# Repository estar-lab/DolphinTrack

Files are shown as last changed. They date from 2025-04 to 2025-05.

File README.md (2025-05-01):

# DolphinTrack

## Computer Vision: Dolphin Detections
`camera_detection`: Includes computer vision pipeline for visual tracking of dolphins. 
- `evaluation`: compares ground truth and tracked coordinates for model performance
- `inference`: pre-trained models, preliminary results, scripts for running different model architectures on input video
- `scripts`: utility files for batching to mitigate RAM issues, prompting for SAM-based models, particle filter to fill in trajectories
- `training_pipeline`: labeled datasets, scripts for fine-tuning model architectures on custom data 

## RF Positioning System: Custom Tag and Anchor Communication 
`RF_localization`: Includes code for ultra-wideband positioning system.
- `anchor_tag_stm32`: code for tag and anchor boards
- `lora_server`: example code for computing position using range transmitted over LoRa
- Also includes BOM, circuit schematics, and CAD for tags and anchors

## Association Demo: Live Person Detection and Localization 
`person_demo`: Includes complete pipeline for real-time detection and tracking of people, with stable association for tagged person.

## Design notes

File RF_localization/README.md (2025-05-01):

# RF Localization Code

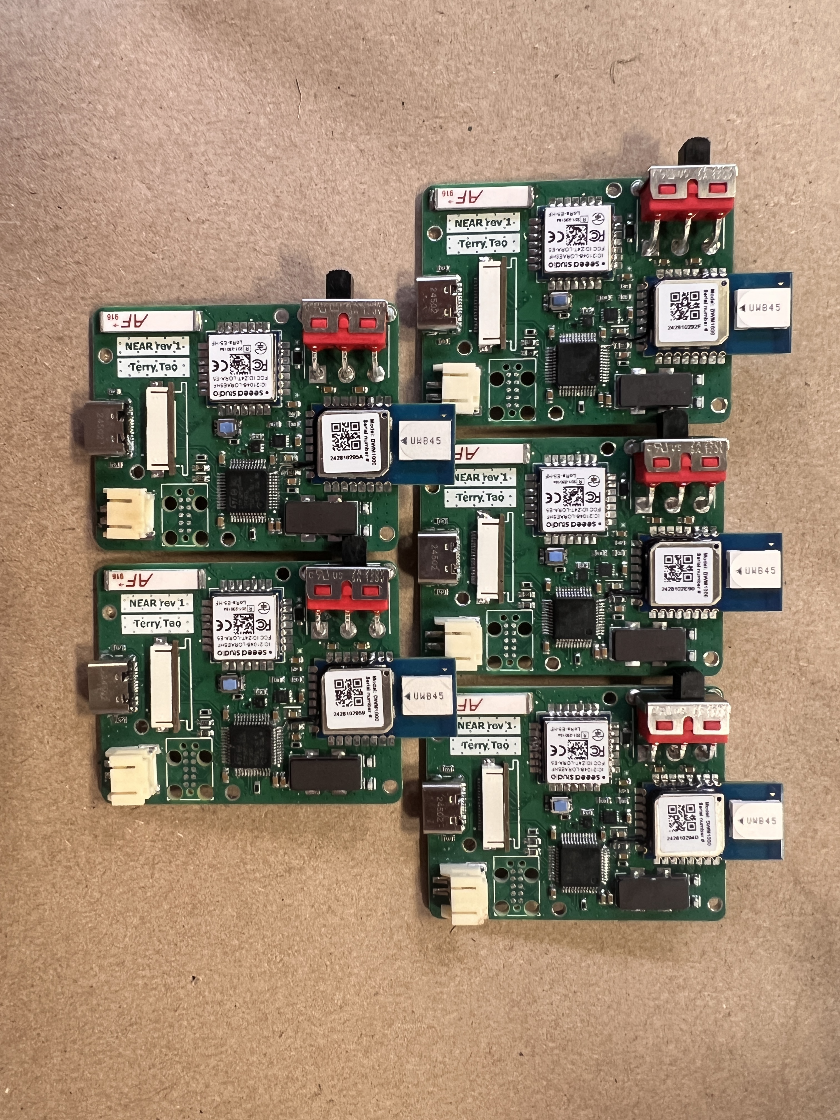
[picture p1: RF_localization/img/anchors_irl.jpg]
anchor_pcbs

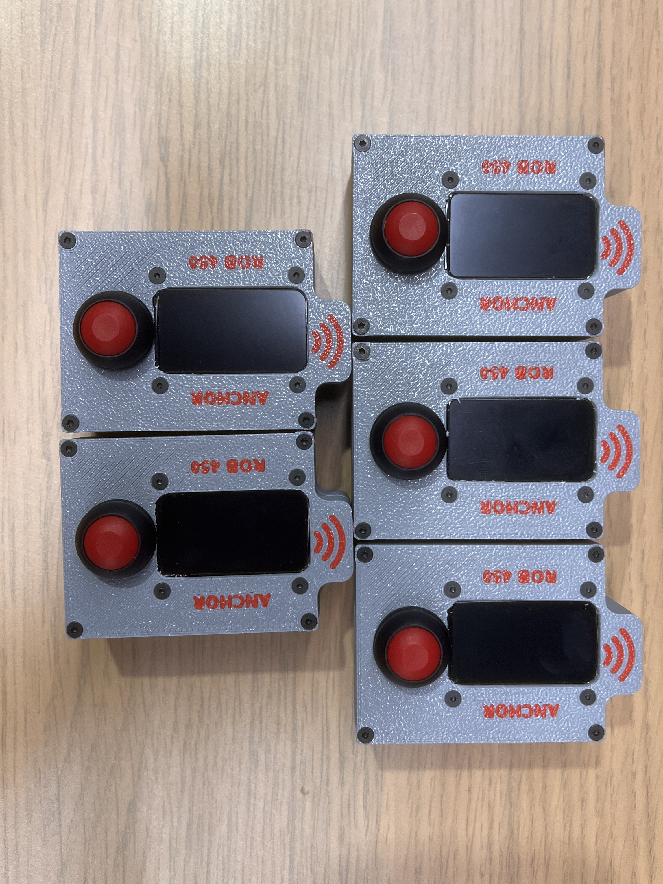
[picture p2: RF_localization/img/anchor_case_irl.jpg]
anchors

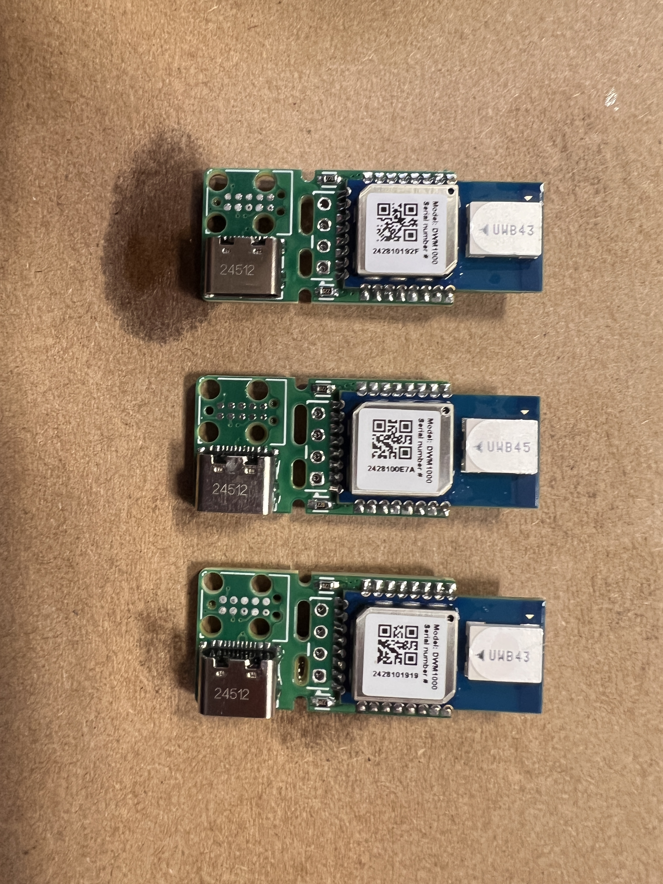
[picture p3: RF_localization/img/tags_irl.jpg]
tags


### anchor_tag_stm32 is for flashing the anchor and tag boards, lora_server is for using the Wio-E5 to receive LoRa messages on the positioning computer. These folders contain more information about setting up software.

### Revisions were made to anchor pcb:

- Reset pin on the DW is now connected to the STM on pin 12
- Screen power mosfet deleted, screen is now powered through two GPIO pins on the STM
- JTAG pogo pin pads moved to the bottom side to make flashing easier when pcb is packaged in case
- 13k pulldown on the ILIM/VSET pin of the BQ instead of 18k to allow for 1.1A battery charge current instead of 0.5A
- 10k pulldown on the TS/MR pin of the BQ bypasses the thermal check to always charge when there is a 5V supply
- Charge diode deleted, originally intended to allow charging when switch is off, didn't work because BQ does voltage regulated charging

### Notes for anchor case assembly:

- The gerber files work for pcbway, layer stack is [SIG TOP, GND, PWR, SIG BOT], and are updated to rev. 2 of the anchor
- Screens are extremely delicate, use caution when pushing on the back because they will crack.
- Bend the button solder terminals 90deg then solder the button wire under them, otherwise the terminal will hit the anchor pcb
- The batteries ship with 2.54 JST, need to recrimp with PH 2.0

### Recommended future changes

- Use a fourth DW message from the anchor to the tag to transmit the calculated range to the tag. UWB transmit rate is much faster than LORA so you can log the position data on the MTAG SD card at a higher rate than the LORA server could receive.
- Change the STMF0 to a faster microcontroller, the DW SPI clock speed is currently 18MHz and this can be increased to at least 20MHz. We have seen forum posts where people have used up to 30MHz, so this is worth trying. (Look out for AndyA on the Decawave forums, he is the goat)
- Glass cover on the anchor case to prevent accidental screen damage
- Automatic anchor position calibration tool. We think the process for anchor calibration should be graphical, where the user proposes estimated anchor positions, then the tool optimizes the graph based on actual anchor-anchor ranges. Additionally, a calibration initialization message would have to be sent to the anchors, probably over LORA downlink to kick them into calibration mode. In calibration mode, the anchors should poll with a timeout then initialize TWR to the next higher anchor ID.
- For changing the STM to an ESP, we recommend modifying port.h to use the ESP HAL library, and deleting any STM autogenerated HAL includes. The other option is to use thotro/arduino-dw1000 library, which we have not tested.

### Recommended anchor placement at Dolphin Quest Oahu:

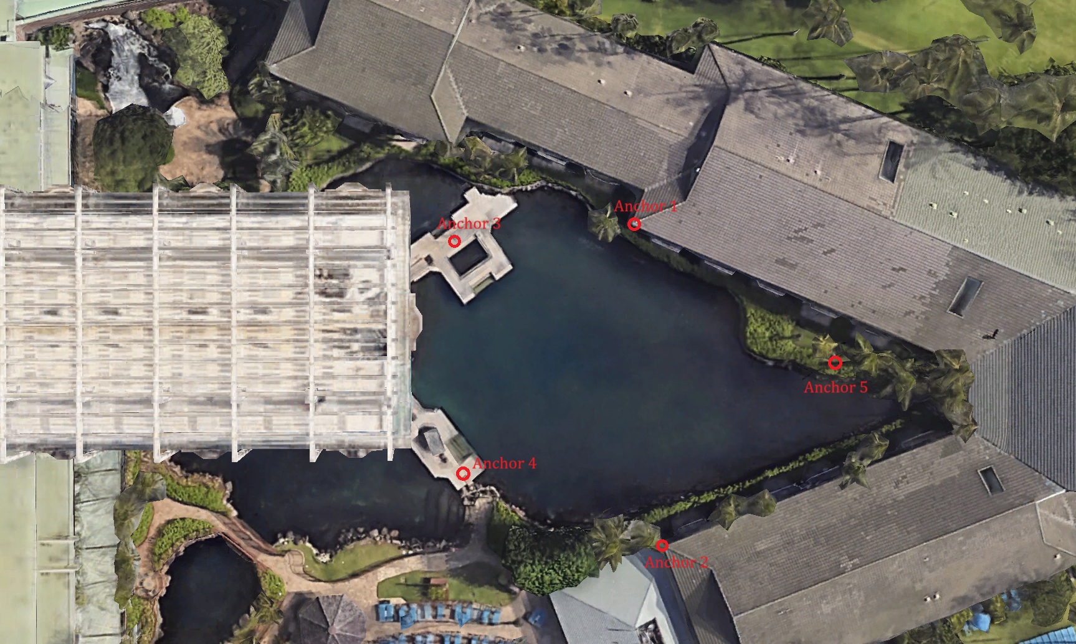
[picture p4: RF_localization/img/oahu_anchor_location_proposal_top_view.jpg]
anchor location proposal top

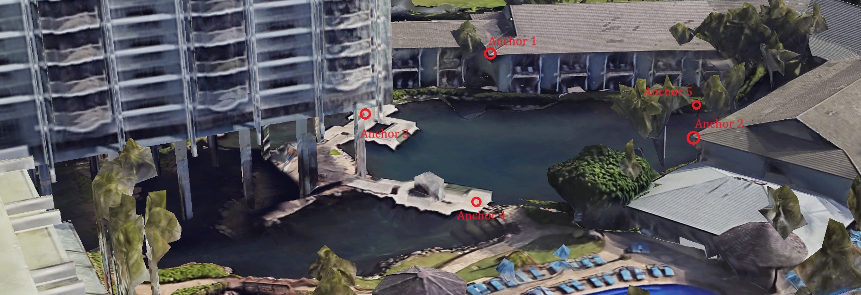
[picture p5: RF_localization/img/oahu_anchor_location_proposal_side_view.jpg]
anchor location proposal side


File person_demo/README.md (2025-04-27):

# Rob 450 Person Tracking Demo 
This code will run a live demo of person tracking intended to demonstrate the efficacy of the DolphinTrack association system 
in a testing environment. 

## Hardware Requirements 
- ZED camera: Used to record video of the testing environment 
- NVIDIA Jetson: Used to run ZED SDK for real-time tracking
- RF tags and anchors: Used for retrieving position coordinates
- Laptop: Used to display particle filter for coordinates received by Jetson 

## Usage 
`association_demo.py`: Used for camera tracking, RF positioning, and association 
- Outputs live video stream of tracked people in camera FOV, each with a unique ID
- Prints live world frame coordinate of person holding RF tag
- Re-associates tagged person, combining camera and RF position to display red bounding box with ID 0
  
`particle_filter.py`: Used for plotting real-time position of tagged person in world frame 
- Receives world frame coordinates of tagged person
- Plots real-time motion of tagged person in world frame 

## Applications 
- Handles dropout and identity switches for tracking scenarios, maintaining consisted ID for tagged person
- Will be used in the field for dolphin tracing and association

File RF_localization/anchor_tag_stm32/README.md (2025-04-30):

# STM32 Anchor and Tag Code

### Setup
1. Clone this repository.
2. Download the STM32CubeIDE (available at https://www.st.com/en/development-tools/stm32cubeide.html).
3. Navigate to `File` -> `Open Projects from File System` -> `Directory`, select this directory (anchor_tag_stm32) in the file system, and click `Finish`.
4. The project should now show up in the `Project Explorer` on the left side of the screen as `NEAR_ANCHOR`. Press `Ctrl+B` or `Project` -> `Build All` to build.

The code for ranging is located in the `Core/` folder. Use the definitions in `Core/Inc/main.h` to determine whether the tag or anchor code is built. The tag and anchor ID's can be configured in `Core/Inc/id.h`. When the STLINK (included with the hardware) is attached to the tag or anchor, press the green play button to flash the device.

### Resources
* This codebase is adapted from the example code available at https://www.decawave.com/wp-content/uploads/2019/01/dw1000_api_rev2p14.zip.
* The DW1000 user manual provides detailed information on using the chip and ranging applications (https://www.qorvo.com/products/p/DW1000#documents).
* The Qorvo forum (https://forum.qorvo.com/tags/c/wireless-connectivity/ultra-wideband/5/dw1000) and in particular the user AndyA (https://forum.qorvo.com/u/andya/summary) made this project possible.
* Information on the LoRa module can be found on the Seeed Studio Wiki (https://wiki.seeedstudio.com/wio_e5_class/).

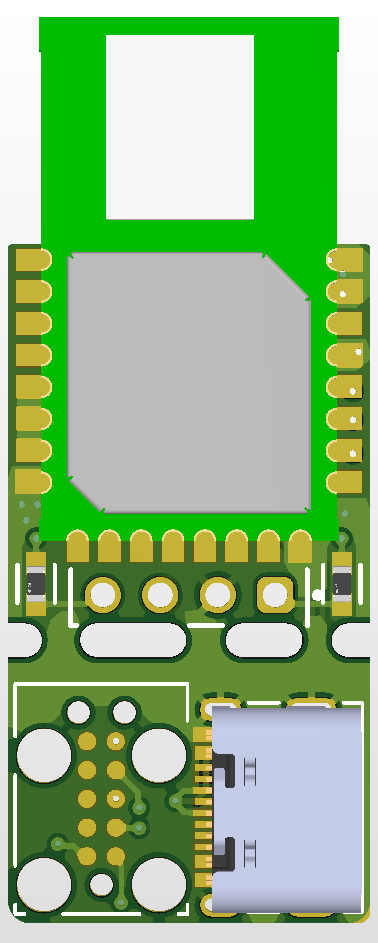
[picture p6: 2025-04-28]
RF_localization/ecad/tag/NEAR_DAUGHTER.png

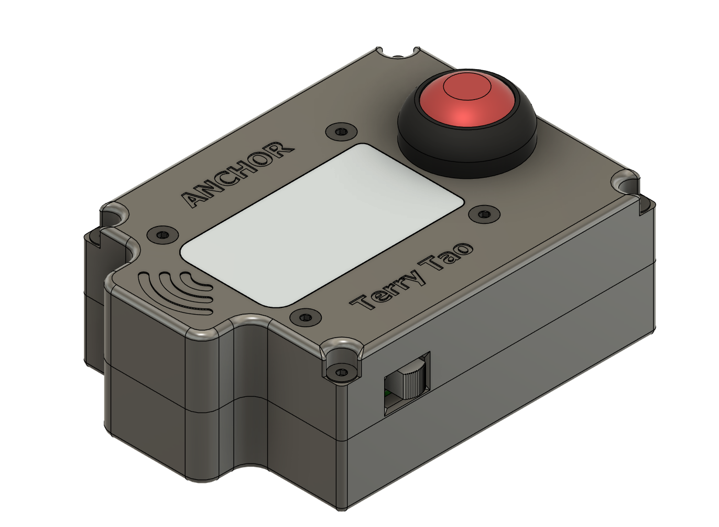
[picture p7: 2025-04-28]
RF_localization/ecad/anchor/CAD_1.png

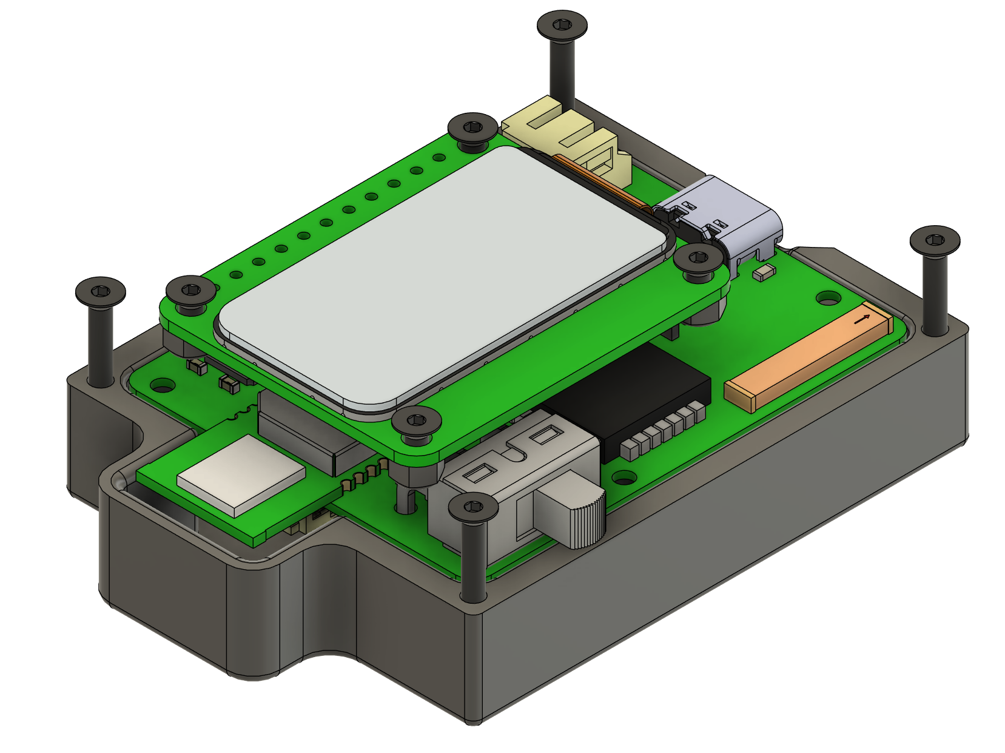
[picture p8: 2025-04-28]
RF_localization/ecad/anchor/CAD_2.png

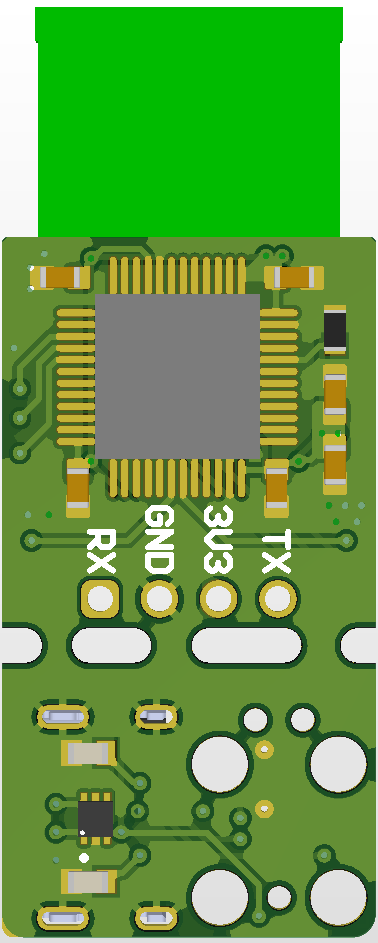
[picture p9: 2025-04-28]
RF_localization/ecad/tag/NEAR_DAUGHTER_BOT.png

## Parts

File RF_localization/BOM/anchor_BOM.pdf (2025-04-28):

Line # | Name | Description | Designator | Revision ID | Revision State | Revision Status | Quantity | Manufacturer 1 | Manufacturer Part Number 1 | Manufacturer Lifecycle 1 | Supplier 1 | Supplier Part Number 1 | Supplier Unit Price 1 | Supplier Subtotal 1
| 1uF | Cap Ceramic 1uF 25V X7R 10% Pad SMD 0603 125C Automotive T/R | C1, C2, C6, C7, C8, C9, C10, C11, C13, C14 | CMP-001-00097-1 | Draft | Up to date | 10 Murata | | GCM188R71E105KA64J | Volume Production | Newark | 66AJ7155 | 0.088 | 0.88
| C0603C120J5GACTU | Ceramic Capacitor 12Pf 50V, C0G, 5%, 0603, Full Reel | C4, C5 | CMP-2006-03703-3 | New From Design | Up to date | | 2 KEMET | C0603C120J5GACTU | Volume Production | Newark | 19C1214 | 0.007 | 0.014
| GRM188R60J106ME47D | Chip Multilayer Ceramic Capacitors for General Purpose, 0603, 10uF, X5R, 15%, 20%, 6.3V | C12 | CMP-2006-02792-2 | New From Design | Up to date | | 1 Murata | GRM188R60J106ME47D | Volume Production | Newark | 24R6334 | 0.065 | 0.065
| TC2050-IDC | CBL PLUG-OF-NAILS 10-PIN W/ LEGS | DBG1 | CMP-002-00071-4 | Draft | Up to date | | 1 Tag-Connect | TC2050-IDC | Volume Production | Digikey | TC2050-IDC-ND | 39 | 39
| ANT-916-CHP-T | 915 MHz Monopole Ceramic Chip Antenna | E1 | CMP-00025-00008-1 | Draft | Up to date | | 1
| 52746-1871 | 0.5 mm Pitch Easy-On(TM) Type FPC Connector, 2.0 mm Mated Height, Right Angle, ZIF, SMT, Bottom Contact, 18 Circuits, -20 to 85 degC, ELV and RoHS Compliant, Tape and Reel | J1 | CMP-1241-00380-1 | Released | Up to date | | 1 Molex | 52746-1871 | Volume Production | Newark | 37AC1285 | 1.29 | 1.29
| 2171790001 | USB Type C -Connector, Top-mount SMT, 16pos | Molex Incorporated 217179-0001 | J2 | CMP-002-00656-1 | Draft | Up to date | | 1
| S2B-PH-SM4-TB | Connector Header Surface Mount, Right Angle 2 position 0.079 (2.00mm) | P1, P2 | CMP-002-00662-3 | Draft | Up to date | | 2
| CPF0603B22RE1 | RES SMD 22Ω 0.1% 1/16W 0603 | R1, R2, R3 | CMP-03211-007811-1 | New From Design | Up to date | | 3 TE Connectivity Neohm | CPF0603B22RE1 | Volume Production | Arrow Electronics | CPF0603B22RE1 | 0.1824 | 0.5472
| ERJ3EKF1002V | Chip Resistor, 10 KOhm, +/- 1%, 0.1 W, -55 to 155 degC, 0603 (1608 Metric), RoHS, Tape and Reel | R4, R5, R14 | CMP-1012-00623-3 | Released | Up to date | | 3 Vishay | CRCW060310K0FKEB | Obsolete | Newark | 96Y9100 | 0.005 | 0.015
| ERJ-3EKF1001V | | R6 | CMP-2000-00180-1 | Released | Up to date | | 1 Panasonic | ERJ-3EKF1001V | Volume Production | Newark | 85Y8498 | 0.098 | 0.098
| Resistor 100k +/-1% 0603 100 mW | Chip Resistor, 100 KOhm, +/- 1%, 0.1 W, -55 to 155 degC, 0603 (1608 Metric) | R7 | CMP-009-00023-4 | Draft | Up to date | | 1 Yageo | RC0603FR-13100KL | Volume Production | Farnell | 2309107 | 0.00892 | 0.0892
| ERA-3AEB133V | RES SMD 13K OHM 0.1% 1/10W 0603 | R8 | CMP-2000-00907-2 | Released | Up to date | | 1 Panasonic | ERA-3AEB133V | Volume Production | Mouser | 667-ERA-3AEB133V | 0.1 | 0.1
| ERJ-3GEYJ301V | | R9 | CMP-2000-00766-1 | Released | Up to date | | 1 Panasonic | ERJ-3GEYJ301V | Volume Production | Digikey | P300GCT-ND | 0.1 | 0.1
| RC0603JR-07200KL | | R10 | CMP-2000-04252-1 | Released | Up to date | | 1 Yageo | RC0603JR-07200KL | Volume Production | Newark | 68R0165 | 0.003 | 0.003
| RC0603FR-075K1L | | R12, R13 | CMP-2000-04091-1 | Released | Up to date | | 2 Yageo | RC0603FR-075K1L | Volume Production | Digikey | 311-5.10KHRCT-ND | 0.009 | 0.09
| 500SSP1S1M6QEA | Slide Switch SPDT Through Hole, Right Angle | S1 | CMP-011-00014-1 | Draft | Up to date | | 1
| TLV70033DSER | Linear Voltage Regulator IC 1 Output 200mA 6-WSON _1.5x1.5_ | U | CMP-019-00083-5 | Draft | Up to date | | 1
| STM32F072CBT6TR | ARM Cortex-M0 32-bit MCU, 128 KB Flash, 16 KB Internal RAM, 37 I/ Os, 48-Pin LQFP, -40 to 85 degC, Tape and Reel | U1 | CMP-0304-00171-1 | Released | Up to date | | 1 STMicroelectronics | STM32F072CBT6TR | Volume Production | Mouser | 511-STM32F072CBT6TR | 4.54 | 4.54
| DWM1000 | 802.15.4 IR-UWB Transceiver Module 3.5GHz ~ 6.5GHz Integrated, Chip Surface Mount | U2 | CMP-236-000000-2 | Draft | Up to date | | 1
| 317990687 | Available No Description | U3 | CMP-031-00023-1 | Draft | Up to date | | 1
| BQ25185DLHR | Available No Description | U4 | CMP-019-00082-1 | Draft | Up to date | | 1
| ABC2-8.000MHZ-4-T | LOW FREQUENCY CERAMIC SURFACE MOUNT MICROPROCESSOR CRYSTAL | Y1 | CMP-003-00037-3 | Draft | Up to date | | 1

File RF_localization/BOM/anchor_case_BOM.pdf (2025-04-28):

Description | Link | Price | QTY | Subtotal | Total

203.32

NOTE: This BOM is for the anchor case, and you can make 5 anchors with it. Seperate pcb and digikey orders needed.

Adafruit

EYESPI Cable - 18-pin 50mm long Flex PCB (FPC) A-B Type | https://www.adafruit.com/product/5462 0.75 | 10 | 7.5
Adafruit 1.47" 320x172 Round Rectangle Color IPS TFT Display - ST7789 | https://www.adafruit.com/product/5393#technical-details 17.5 | 5 | 87.5

Mcmaster
Black-Oxide Alloy Steel Hex Drive Flat Head Screw
90 Degree Countersink, M2 x 0.40 mm Thread, 20 mm Long | https://www.mcmaster.com/91294A539/ 11 | 1 | 11
Black-Oxide Alloy Steel Hex Drive Flat Head Screw
90 Degree Countersink Angle, M2 x 0.40 mm Thread, 6 mm Long | https://www.mcmaster.com/91294A004/ 8.75 | 1 | 8.75
Black-Oxide Steel Hex Nut
Medium-Strength, Class 8, M2 x 0.4 mm Thread | https://www.mcmaster.com/90593A024/ 7.35 | 1 | 7.35

Amazon
20 Sets Mini Micro Jst 2.0 Ph 2-Pin Connector Plug Male with 150mm Cable & Female | https://www.amazon.com/daier-Micro-2-Pin-Connector-Female/dp/B01DUC1O68/ref=sr_1_14?crid=VO3YZ7KHXA2Y&dib=eyJ2IjoiMSJ9.9sJKZ5FwtJ4kze1BA345YCPioqQOVa-VaqABd3TGXBfEjGhJVQTjYmEi8gPg798RSTFiWkLwseddpOjzPYxeaQoRiAuzxD9iU7Qdae0v96nsjbxtJA8fFcJF80BcwL9MW--3md1YYNEygBu0XSi_IcoT7NrnOoTF04JuvVOZezy8xe7SFaKCmY-MfA6BU3J-M-eStie89DHCwDwqnO57xkUWAsu5kvBBR8q-TYXmiNw.zfWG2X_bmrrW4oWplgjwqx6AyFNgj9kJcaxIAIPYQe8&dib_tag=se&keywords=ph+connector&qid=1740001482&sprefix=ph+connector%2Caps%2C106&sr=8-14 8.59 | 1 | 8.59
KBT 3.7V 1200mAh Li-Polymer Battery: 103040 Lipo Rechargeable Lithium-ion Replacement Batteries with PH 2.54 JST Connector, PH1.25/2.0 JST Connector for Replacement - 8Pack https://www.amazon.com/KBT-3-7V-1200mAh-Li-Polymer-Battery/dp/B0BJPSPMVZ/ref=sr_1_54_sspa?crid=WLEHHBF2CQX6&keywords=battery%2B2.0-JST&qid=1740001852&sprefix=battery%2B2.0-jst%2Celectronics%2C95&sr=8-54-spons&xpid=sxqcT81pwW_7L&sp_csd=d2lkZ2V0TmFtZT1zcF9tdGY&th=1 42.99 | 1 | 42.99
JST PH 2.0 mm Pitch 2-Pin | https://www.amazon.com/CQRobot-Pieces-Connector-Housing-Adapter/dp/B09DP9FZTX/ref=sr_1_3?crid=1NVVEX9YAPEZX&dib=eyJ2IjoiMSJ9.gLALRR5R8nvXmK7_aX-SVLhRuu-9eLUFIJZSYCB94VZoZ786LtH-7nKPzHgF2yqeBVABtV4f0GRSLhmuPMA2PtQo6SKT8OZTBjnt2_7Z5oEUyrHXIDuLu3DujMhuPlNAO6hYjSAGM8jQ9ym_JzQ9Ny0nJkxK9pEeAfdy3hGa2wESgRZuGOhmzF65ui-byTT0p77pdiOj9J7HXta8dGLsivxQKAKZe8getvdQvUJCeZI.0Qwiy6H9vZdWyn26awKfNayb3ZjnXloC8zJi07ltU2s&dib_tag=se&keywords=ph%2B2.0%2Bcrimp&qid=1745807585&sprefix=ph%2B2.0%2Bcrimp%2Caps%2C73&sr=8-3&th=1 5.99 | 1 | 5.99

Digikey
SWITCH PB SPST-NO 0.125A 125V | https://www.digikey.com/en/products/detail/e-switch/RP8100B2M1CEBLKREDNIL/4029115 4.73 | 5 | 23.65

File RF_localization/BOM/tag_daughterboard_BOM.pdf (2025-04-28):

Line # | Name | Description | Designator | Revision ID | Revision State | Revision Status | Quantity | Manufacturer 1 | Manufacturer Part Number 1 | Manufacturer Lifecycle 1 | Supplier 1 | Supplier Part Number 1 | Supplier Unit Price 1 | Supplier Subtotal 1
| 1uF | Cap Ceramic 1uF 25V X7R 10% Pad SMD 0603 125C Automotive T/R | C1, C2, C6, C7, C8, C9 | CMP-001-00097-1 | Draft | Up to date | 6 | Murata | GCM188R71E105KA64J | Volume Production | Newark | 66AJ7155 | 0.088 | 0.88
| TC2050-IDC | CBL PLUG-OF-NAILS 10-PIN W/ LEGS | DBG1 | CMP-002-00071-4 | Draft | Up to date | 1 | Tag-Connect | TC2050-IDC | Volume Production | Digikey | TC2050-IDC-ND | 39 | 39
| 2171790001 | USB Type C -Connector, Top-mount SMT, 16pos | Molex Incorporated 217179-0001 | J2 | CMP-002-00656-1 | Draft | Up to date | 1
| 61300411121 | WR-PHD Pin Header, THT, Vertical, pitch 2.54mm, 1 Row, 4P | P1 | CMP-002-00283-1 | Draft | Up to date | 1 | Wurth Electronics | 61300411121 | Volume Production | Digikey | 732-5317-ND | 0.17 | 0.17
| CPF0603B22RE1 | RES SMD 22Ω 0.1% 1/16W 0603 | R2, R3 | CMP-03211-007811-1 | New From Design | Up to date | 2 | TE Connectivity Neohm | CPF0603B22RE1 | Volume Production | Arrow Electronics | CPF0603B22RE1 | 0.1824 | 0.3648
| ERJ3EKF1002V | Chip Resistor, 10 KOhm, +/- 1%, 0.1 W, -55 to 155 degC, 0603 (1608 Metric), RoHS, Tape and Reel | R5 | CMP-1012-00623-3 | Released | Up to date | 1 | Vishay | CRCW060310K0FKEB | Obsolete | Newark | 96Y9100 | 0.005 | 0.005
| RC0603FR-075K1L | | R12, R13 | CMP-2000-04091-1 | Released | Up to date | 2 | Yageo | RC0603FR-075K1L | Volume Production | Digikey | 311-5.10KHRCT-ND | 0.009 | 0.09
| TLV70033DSER | Linear Voltage Regulator IC 1 Output 200mA 6-WSON _1.5x1.5_ | U | CMP-019-00083-5 | Draft | Up to date | 1
| STM32F072CBT6TR | ARM Cortex-M0 32-bit MCU, 128 KB Flash, 16 KB Internal RAM, 37 I/ Os, 48-Pin LQFP, -40 to 85 degC, Tape and Reel | U1 | CMP-0304-00171-1 | Released | Up to date | 1 | STMicroelectronics | STM32F072CBT6TR | Volume Production | Mouser | 511-STM32F072CBT6TR | 4.54 | 4.54
| DWM1000 | 802.15.4 IR-UWB Transceiver Module 3.5GHz ~ 6.5GHz Integrated, Chip Surface Mount | U2 | CMP-236-000000-2 | Draft | Up to date | 1

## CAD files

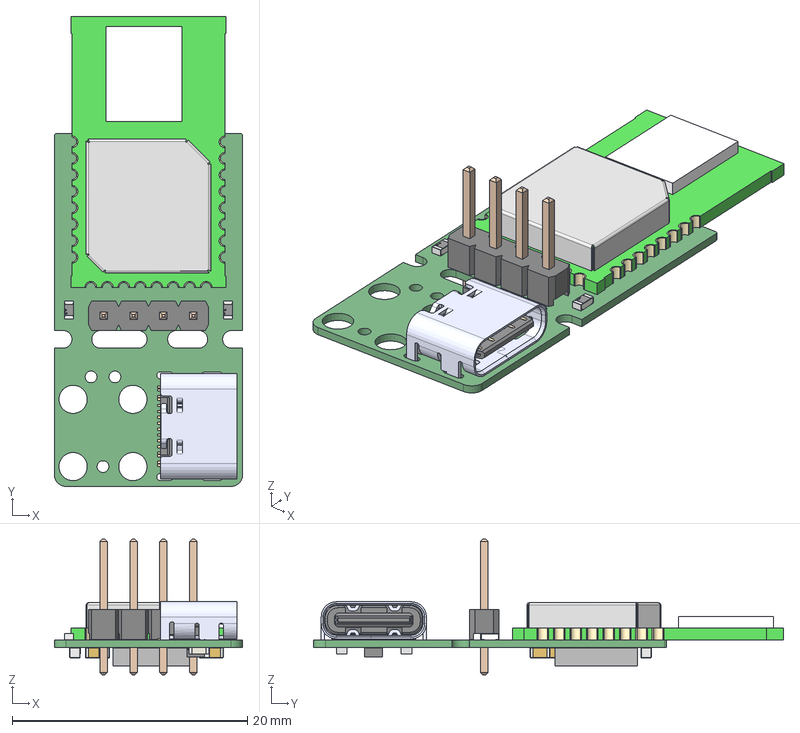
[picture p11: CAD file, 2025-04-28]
RF_localization/ecad/anchor/NEAR_DAUGHTER.step
16.0 x 39.9 x 11.5 mm
TLV70033DSER
DWM1000--3DModel-STEP-56544
Extruded x 7
Mid_Body
Mark
TE connectivity Logo 1 x 2
6130xx11121_PIN x 4

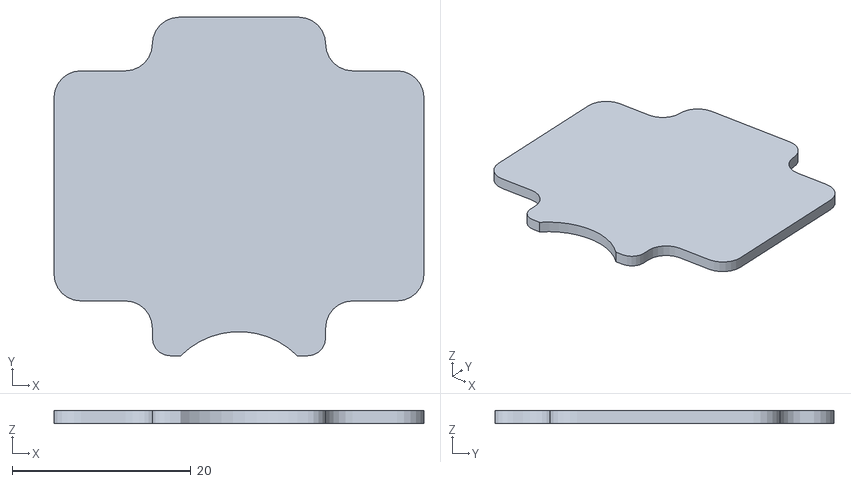
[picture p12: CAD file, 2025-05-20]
RF_localization/mcad/anchor-screen-cover.stl
41.4 x 37.9 x 1.50

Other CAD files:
RF_localization/mcad/tag_daughterboard.step
RF_localization/mcad/anchor-screen-cover.dwg
RF_localization/mcad/anchor-screen-cover.ipt

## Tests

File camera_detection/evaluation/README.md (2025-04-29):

# Evaluating Visual Tracking Results 

## Steps to make comparison 
1. Run `annotate_frames.py`: plot ground truth coordinates for each dolphin in video -- results in `ground_truth_centroids.json`
2. Run `inference` for model: run inference on video for model architecture -- results in `tracked_centroids.json`
3. Run `plot_coordinates.py`: plots positions over time of dolphins (from ground truth or tracked)
4. Run `compare_centroids.py`: compares ground truth and tracked coordinates to understand model performance

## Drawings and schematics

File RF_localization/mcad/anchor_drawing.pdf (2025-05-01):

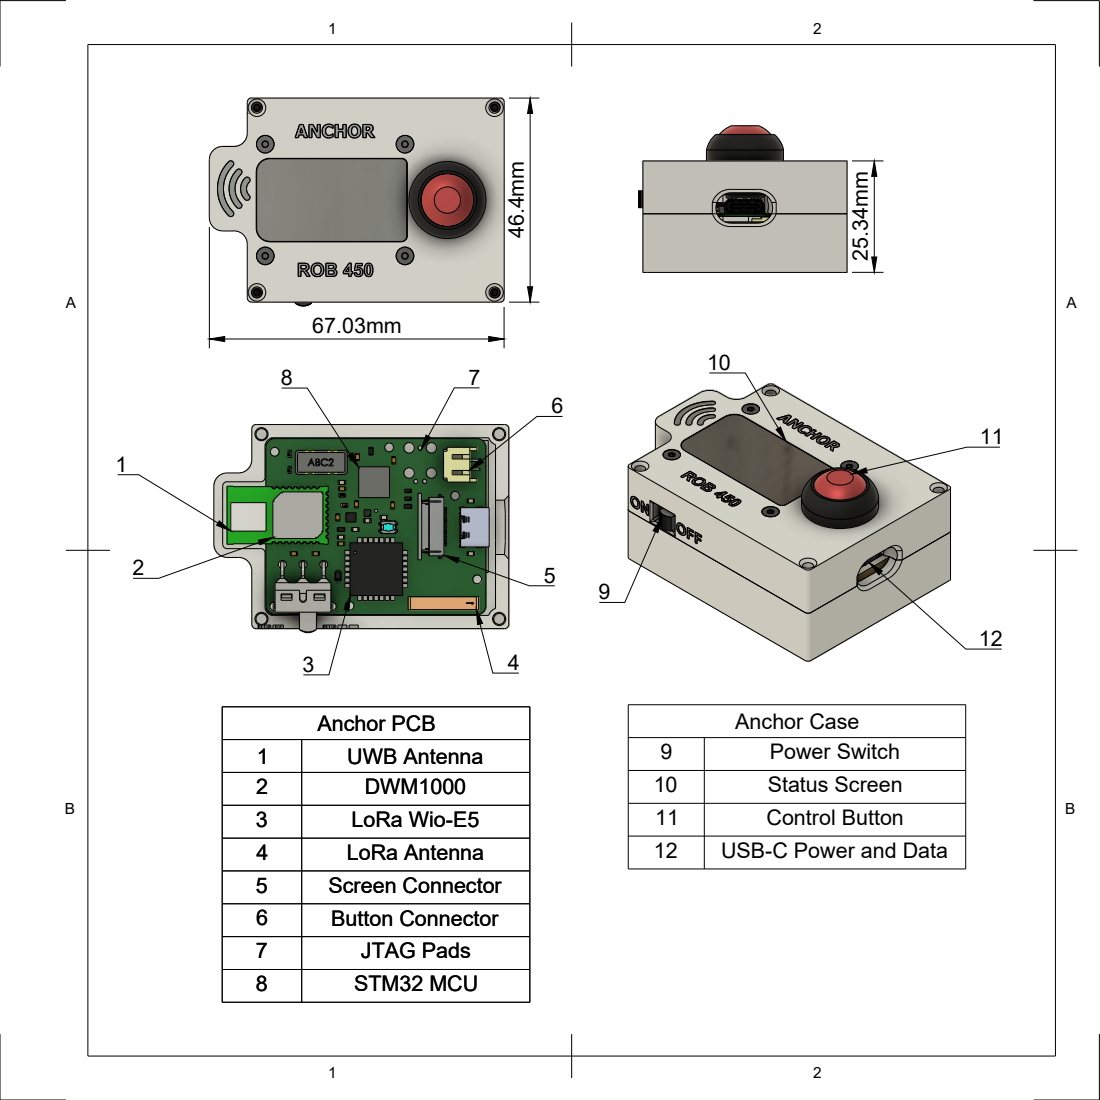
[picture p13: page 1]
Anchor PCB; UWB Antenna; LoRa Wio-E5; LoRa Antenna; Screen Connector; Button Connector; JTAG Pads; STM32 MCU; Anchor Case; Power Switch; Status Screen; Control Button; USB-C Power and Data

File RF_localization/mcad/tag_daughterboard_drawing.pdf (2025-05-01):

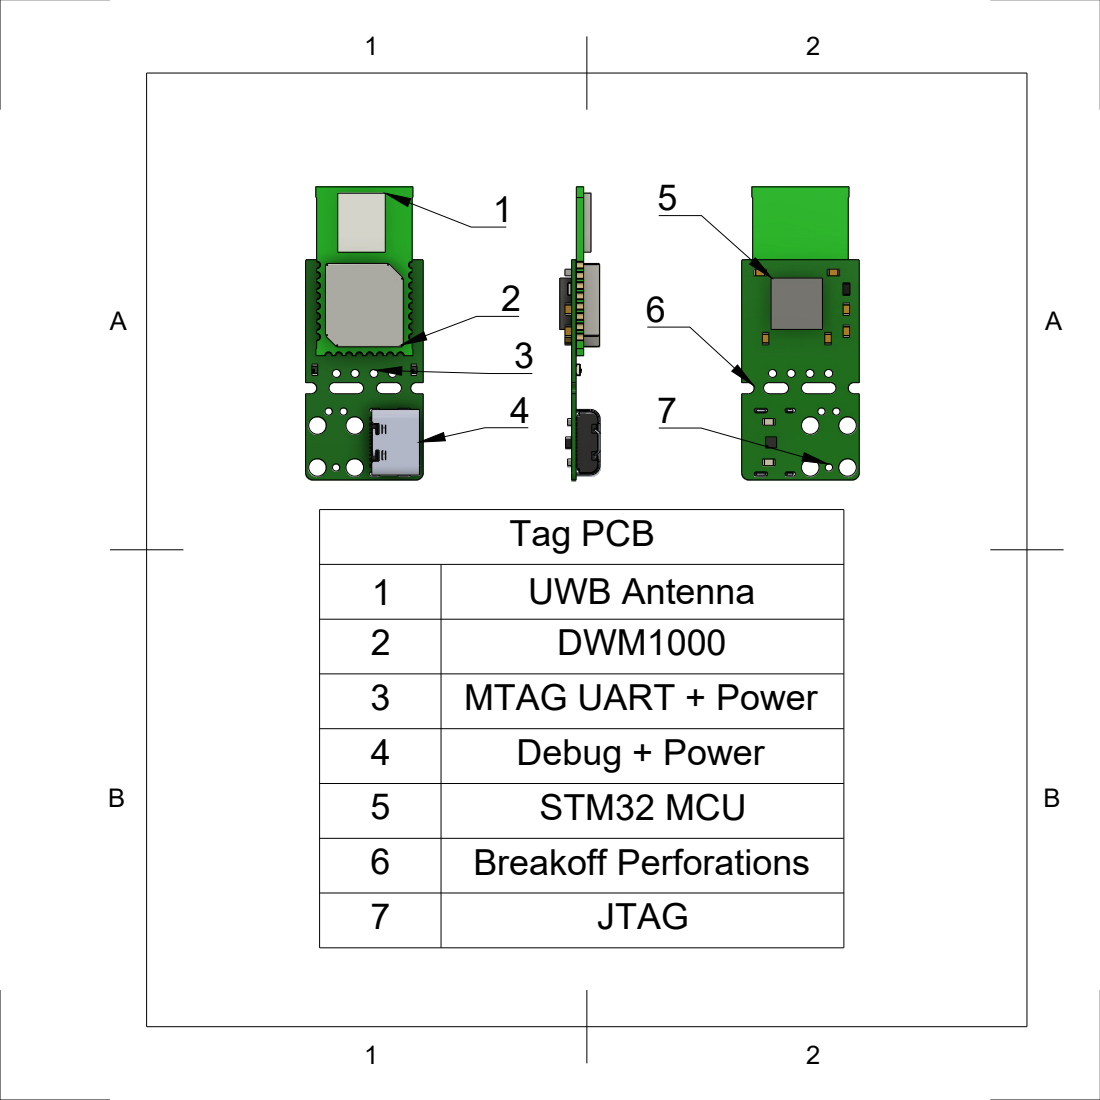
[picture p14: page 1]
Tag PCB

1 | UWB Antenna
2 | DWM1000
3 | MTAG UART + Power
4 | Debug + Power
5 | STM32 MCU
6 | Breakoff Perforations
7 | JTAG

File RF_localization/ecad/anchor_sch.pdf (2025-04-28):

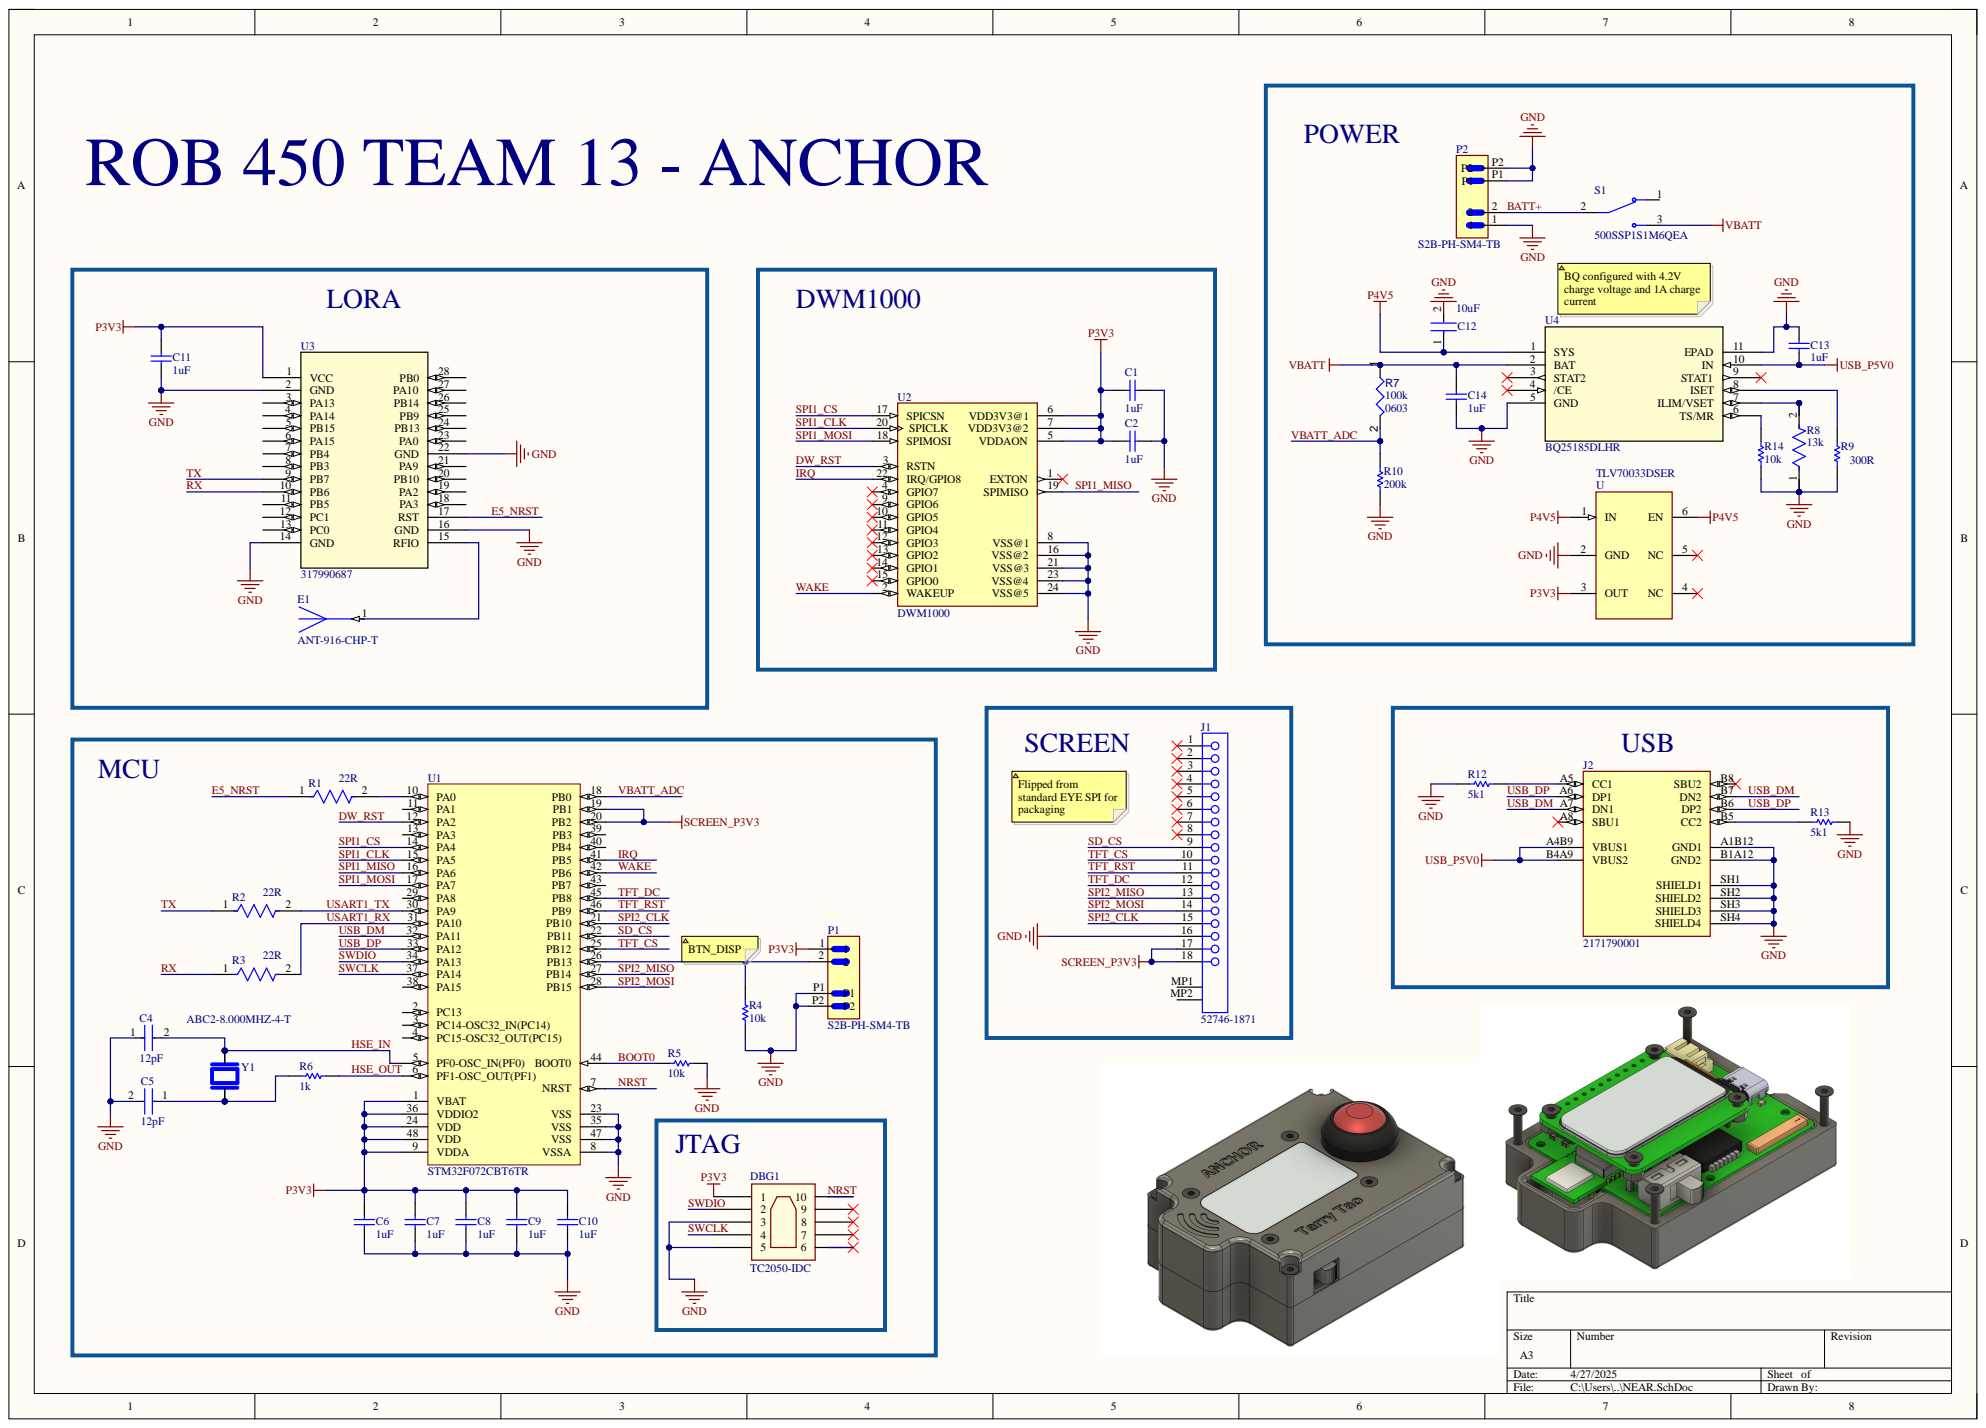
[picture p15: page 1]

BQ configured with 4.2V
charge voltage and 1A charge
current

Flipped from
standard EYE SPI for
packaging

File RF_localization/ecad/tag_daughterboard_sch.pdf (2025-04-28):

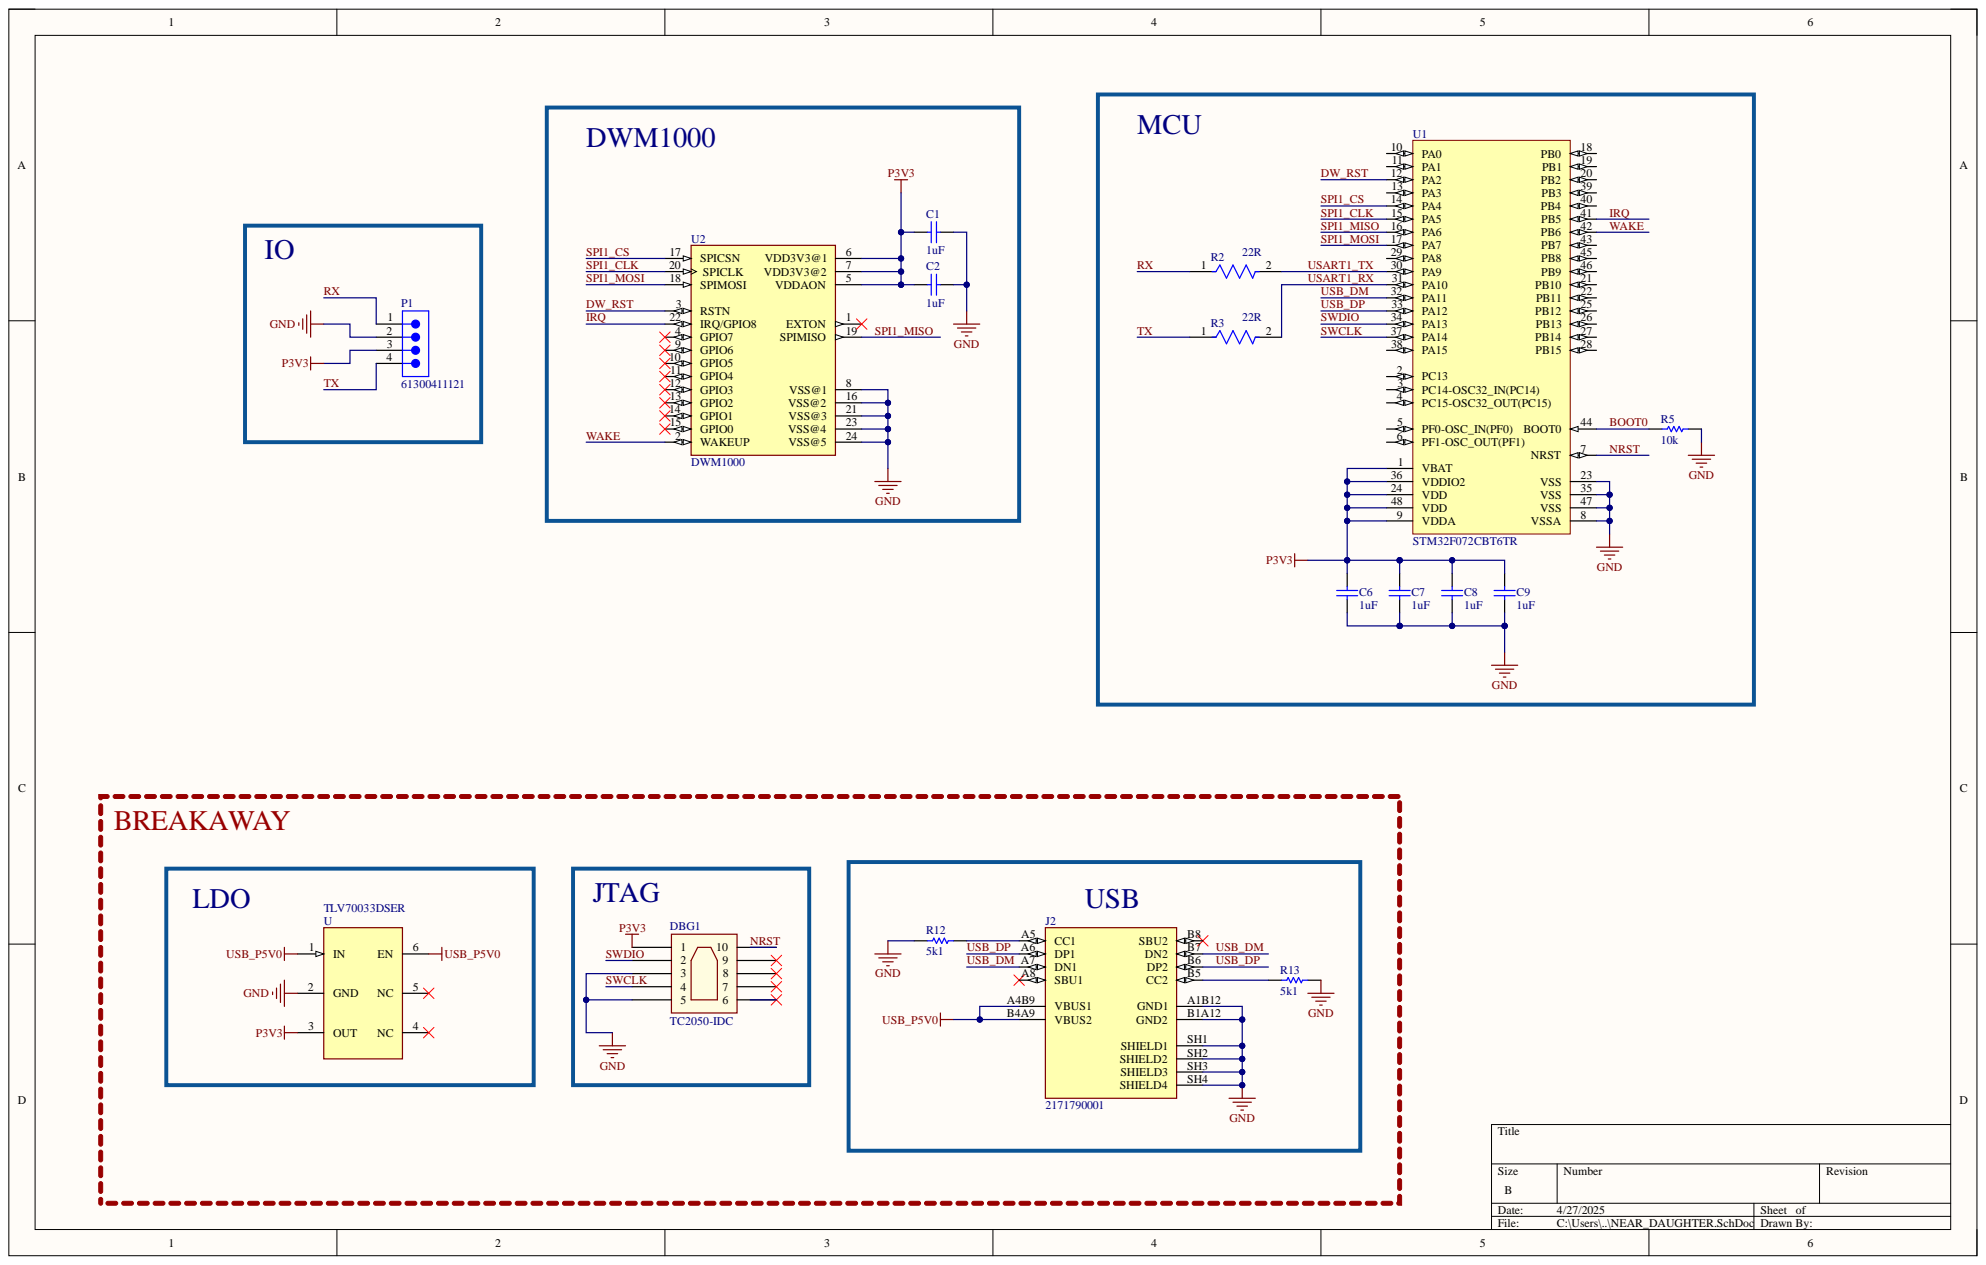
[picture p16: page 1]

Size B | Number | Revision

Date: 4/27/2025 | Sheet of
File: C:\Users\..\NEAR_DAUGHTER.SchDoc | Drawn By:

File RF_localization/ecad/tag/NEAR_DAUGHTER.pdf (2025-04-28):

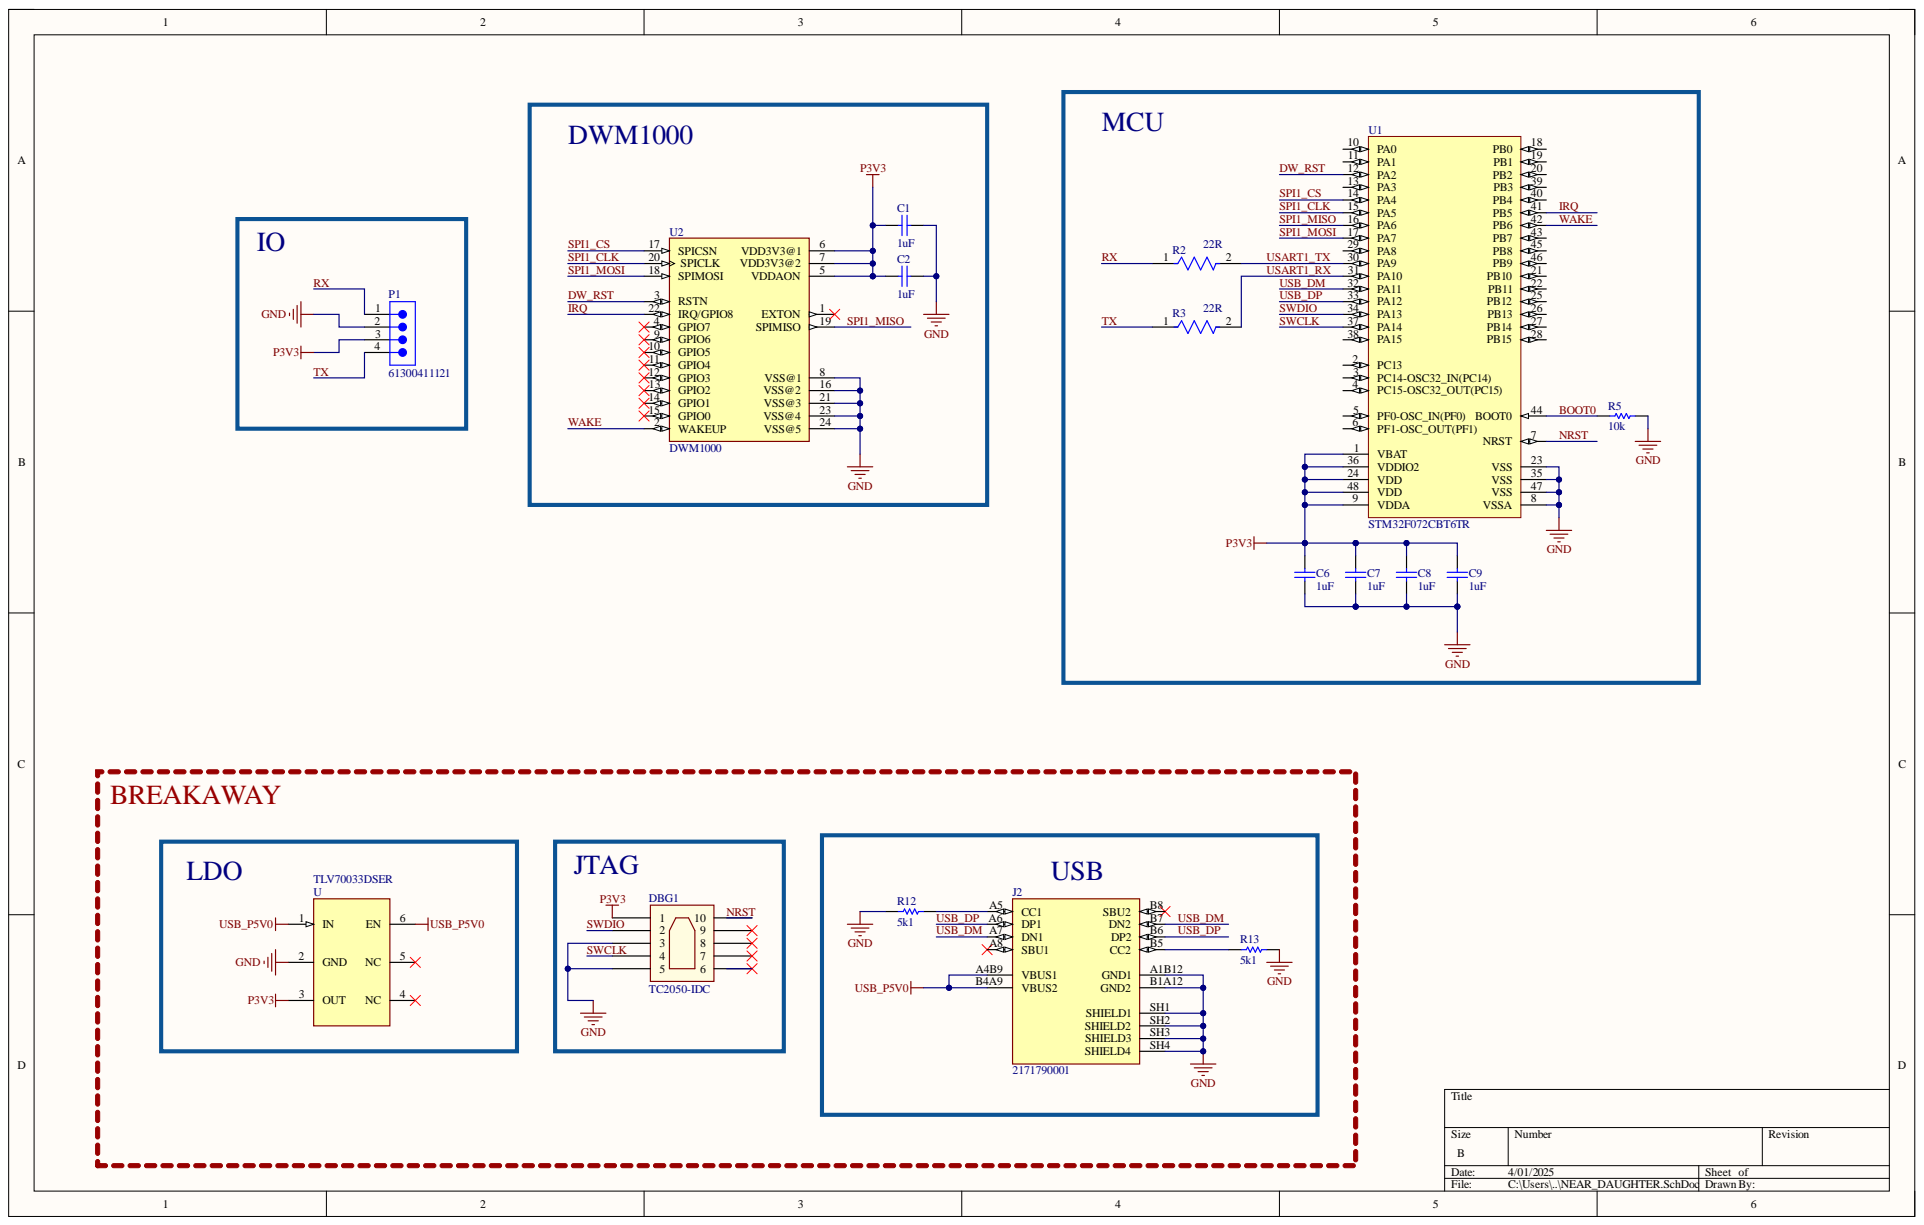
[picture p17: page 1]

Size B | Number | Revision

Date: 4/01/2025 | Sheet of
File: C:\Users\..\NEAR_DAUGHTER.SchDoc | Drawn By:

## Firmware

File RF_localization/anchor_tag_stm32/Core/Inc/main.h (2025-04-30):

/* USER CODE BEGIN Header */
/**
  ******************************************************************************
  * @file           : main.h
  * @brief          : Header for main.c file.
  *                   This file contains the common defines of the application.
  ******************************************************************************
  * @attention
  *
  * Copyright (c) 2025 STMicroelectronics.
  * All rights reserved.
  *
  * This software is licensed under terms that can be found in the LICENSE file
  * in the root directory of this software component.
  * If no LICENSE file comes with this software, it is provided AS-IS.
  *
  ******************************************************************************
  */
/* USER CODE END Header */

/* Define to prevent recursive inclusion -------------------------------------*/
#ifndef __MAIN_H
#define __MAIN_H

#ifdef __cplusplus
extern "C" {
#endif

/* Includes ------------------------------------------------------------------*/
#include "stm32f0xx_hal.h"

/* Private includes ----------------------------------------------------------*/
/* USER CODE BEGIN Includes */

#include "port.h"

#define ANT_DLY 16433 // Can be tuned to improve ranging accuracy, default was16436

/* Select whether to flash the tag or anchor here */
//#define FLASH_TAG
#define FLASH_ANCHOR

/* USER CODE END Includes */

/* Exported types ------------------------------------------------------------*/
/* USER CODE BEGIN ET */

/* USER CODE END ET */

/* Exported constants --------------------------------------------------------*/
/* USER CODE BEGIN EC */

/* USER CODE END EC */

/* Exported macro ------------------------------------------------------------*/
/* USER CODE BEGIN EM */

/* USER CODE END EM */

/* Exported functions prototypes ---------------------------------------------*/
void Error_Handler(void);

/* USER CODE BEGIN EFP */

/* USER CODE END EFP */

/* Private defines -----------------------------------------------------------*/
#define E5_NRST_Pin GPIO_PIN_0
#define E5_NRST_GPIO_Port GPIOA
#define DW_RESET_Pin GPIO_PIN_2
#define DW_RESET_GPIO_Port GPIOA
#define DW_RESET_EXTI_IRQn EXTI2_3_IRQn
#define DW_NSS_Pin GPIO_PIN_4
#define DW_NSS_GPIO_Port GPIOA
#define DW_SCK_Pin GPIO_PIN_5
#define DW_SCK_GPIO_Port GPIOA
#define DW_MISO_Pin GPIO_PIN_6
#define DW_MISO_GPIO_Port GPIOA
#define DW_MOSI_Pin GPIO_PIN_7
#define DW_MOSI_GPIO_Port GPIOA
#define VBATT_ADC_Pin GPIO_PIN_0
#define VBATT_ADC_GPIO_Port GPIOB
#define SCREEN_EN_AUX_Pin GPIO_PIN_1
#define SCREEN_EN_AUX_GPIO_Port GPIOB
#define SCREEN_EN_Pin GPIO_PIN_2
#define SCREEN_EN_GPIO_Port GPIOB
#define SD_CS_Pin GPIO_PIN_11
#define SD_CS_GPIO_Port GPIOB
#define TFT_CS_Pin GPIO_PIN_12
#define TFT_CS_GPIO_Port GPIOB
#define BTN_DISP_Pin GPIO_PIN_13
#define BTN_DISP_GPIO_Port GPIOB
#define DW_IRQn_Pin GPIO_PIN_5
#define DW_IRQn_GPIO_Port GPIOB
#define DW_IRQn_EXTI_IRQn EXTI4_15_IRQn
#define WAKE_Pin GPIO_PIN_6
#define WAKE_GPIO_Port GPIOB
#define TFT_DC_Pin GPIO_PIN_8
#define TFT_DC_GPIO_Port GPIOB
#define TFT_RST_Pin GPIO_PIN_9
#define TFT_RST_GPIO_Port GPIOB

/* USER CODE BEGIN Private defines */

/* USER CODE END Private defines */

#ifdef __cplusplus
}
#endif

#endif /* __MAIN_H */

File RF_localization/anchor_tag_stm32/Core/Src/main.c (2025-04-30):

/* USER CODE BEGIN Header */
/**
 **************w***************************************************************
 * @file           : main.c
 * @brief          : Main program body
 ******************************************************************************
 * @attention
 *
 * Copyright (c) 2025 STMicroelectronics.
 * All rights reserved.
 *
 * This software is licensed under terms that can be found in the LICENSE file
 * in the root directory of this software component.
 * If no LICENSE file comes with this software, it is provided AS-IS.
 *
 ******************************************************************************
 */
/* USER CODE END Header */
/* Includes ------------------------------------------------------------------*/
#include "main.h"
#include "usb_device.h"

/* Private includes ----------------------------------------------------------*/
/* USER CODE BEGIN Includes */

#include "lcd.h"

/* USER CODE END Includes */

/* Private typedef -----------------------------------------------------------*/
/* USER CODE BEGIN PTD */

/* USER CODE END PTD */

/* Private define ------------------------------------------------------------*/
/* USER CODE BEGIN PD */
#define UART_RX_BUF_SIZE 1024
/* USER CODE END PD */

/* Private macro -------------------------------------------------------------*/
/* USER CODE BEGIN PM */

/* USER CODE END PM */

/* Private variables ---------------------------------------------------------*/
ADC_HandleTypeDef hadc;

SPI_HandleTypeDef hspi1;
SPI_HandleTypeDef hspi2;
DMA_HandleTypeDef hdma_spi2_tx;

TIM_HandleTypeDef htim3;

UART_HandleTypeDef huart1;
DMA_HandleTypeDef hdma_usart1_rx;

/* USER CODE BEGIN PV */

/* USER CODE END PV */

/* Private function prototypes -----------------------------------------------*/
void SystemClock_Config(void);
static void MX_GPIO_Init(void);
static void MX_DMA_Init(void);
static void MX_USART1_UART_Init(void);
static void MX_SPI1_Init(void);
static void MX_ADC_Init(void);
static void MX_SPI2_Init(void);
static void MX_TIM3_Init(void);
/* USER CODE BEGIN PFP */

/* Sends AT commands over UART to the LoRa module */
void send_at_msg(char *msg)
{
  HAL_UART_Transmit_IT(&huart1, (uint8_t *)msg, strlen(msg));
}

void (*send_at_msg_ptr)(char *msg);

/* USER CODE END PFP */

/* Private user code ---------------------------------------------------------*/
/* USER CODE BEGIN 0 */

USBD_HandleTypeDef hUSBDDevice;
uint8_t uart_rx_buf[UART_RX_BUF_SIZE];

bool joined = 0;

char joined_msg[] = "+JOIN: Network joined";

/* USER CODE END 0 */

/**
  * @brief  The application entry point.
  * @retval int
  */
int main(void)
{

  /* USER CODE BEGIN 1 */
  send_at_msg_ptr = &send_at_msg;

  /* USER CODE END 1 */

  /* MCU Configuration--------------------------------------------------------*/

  /* Reset of all peripherals, Initializes the Flash interface and the Systick. */
  HAL_Init();

  /* USER CODE BEGIN Init */

  /* USER CODE END Init */

  /* Configure the system clock */
  SystemClock_Config();

  /* USER CODE BEGIN SysInit */

  /* USER CODE END SysInit */

  /* Initialize all configured peripherals */
  MX_GPIO_Init();
  MX_DMA_Init();
  MX_USART1_UART_Init();
  MX_SPI1_Init();
  MX_ADC_Init();
  MX_SPI2_Init();
  MX_USB_DEVICE_Init();
  MX_TIM3_Init();
  /* USER CODE BEGIN 2 */

  // Power to screen
  HAL_GPIO_WritePin(SCREEN_EN_GPIO_Port, SCREEN_EN_Pin, GPIO_PIN_SET);
  HAL_GPIO_WritePin(SCREEN_EN_AUX_GPIO_Port, SCREEN_EN_AUX_Pin, GPIO_PIN_SET);

  LCD_init();

  // Startup sequence for LoRa module
  HAL_GPIO_WritePin(E5_NRST_GPIO_Port, E5_NRST_Pin, GPIO_PIN_SET);
  HAL_Delay(2000);
  HAL_GPIO_WritePin(E5_NRST_GPIO_Port, E5_NRST_Pin, GPIO_PIN_RESET);
  HAL_Delay(100);
  HAL_GPIO_WritePin(E5_NRST_GPIO_Port, E5_NRST_Pin, GPIO_PIN_SET);
  HAL_Delay(100);

  // LoRa command reception callback
  HAL_UARTEx_ReceiveToIdle_DMA(&huart1, uart_rx_buf, UART_RX_BUF_SIZE);

  // Startup lcd text

  UG_FontSetTransparency(1);
  UG_FillScreen(C_BLACK);

  LCD_PutStr(50, 20, "NEAR ANCHOR", FONT_16X26, C_WHITE, C_BLACK);
  LCD_PutStr(50, 50, "DESIGNED BY:", FONT_16X26, C_WHITE, C_BLACK);
  LCD_PutStr(50, 80, "TERRY TAO", FONT_16X26, C_WHITE, C_BLACK);
  LCD_PutStr(50, 110, "THOR HELGESON", FONT_16X26, C_WHITE, C_BLACK);

#ifdef FLASH_TAG
  tag_main();
#endif

#ifdef FLASH_ANCHOR
  anchor_main(send_at_msg_ptr);
#endif

  /* USER CODE END 2 */

  /* Infinite loop */
  /* USER CODE BEGIN WHILE */

  while (1)
  {

    /* USER CODE END WHILE */

    /* USER CODE BEGIN 3 */
  }
  /* USER CODE END 3 */
}

/**
  * @brief System Clock Configuration
  * @retval None
  */
void SystemClock_Config(void)
{
  RCC_OscInitTypeDef RCC_OscInitStruct = {0};
  RCC_ClkInitTypeDef RCC_ClkInitStruct = {0};
  RCC_PeriphCLKInitTypeDef PeriphClkInit = {0};

  /** Initializes the RCC Oscillators according to the specified parameters
  * in the RCC_OscInitTypeDef structure.
  */
  RCC_OscInitStruct.OscillatorType = RCC_OSCILLATORTYPE_HSI|RCC_OSCILLATORTYPE_HSI14
                              |RCC_OSCILLATORTYPE_HSI48;
  RCC_OscInitStruct.HSIState = RCC_HSI_ON;
  RCC_OscInitStruct.HSI48State = RCC_HSI48_ON;
  RCC_OscInitStruct.HSI14State = RCC_HSI14_ON;
  RCC_OscInitStruct.HSICalibrationValue = RCC_HSICALIBRATION_DEFAULT;
  RCC_OscInitStruct.HSI14CalibrationValue = 16;
  RCC_OscInitStruct.PLL.PLLState = RCC_PLL_ON;
  RCC_OscInitStruct.PLL.PLLSource = RCC_PLLSOURCE_HSI;
  RCC_OscInitStruct.PLL.PLLMUL = RCC_PLL_MUL9;
  RCC_OscInitStruct.PLL.PREDIV = RCC_PREDIV_DIV2;
  if (HAL_RCC_OscConfig(&RCC_OscInitStruct) != HAL_OK)
  {
    Error_Handler();
  }

  /** Initializes the CPU, AHB and APB buses clocks
  */
  RCC_ClkInitStruct.ClockType = RCC_CLOCKTYPE_HCLK|RCC_CLOCKTYPE_SYSCLK
                              |RCC_CLOCKTYPE_PCLK1;
  RCC_ClkInitStruct.SYSCLKSource = RCC_SYSCLKSOURCE_PLLCLK;
  RCC_ClkInitStruct.AHBCLKDivider = RCC_SYSCLK_DIV1;
  RCC_ClkInitStruct.APB1CLKDivider = RCC_HCLK_DIV1;

  if (HAL_RCC_ClockConfig(&RCC_ClkInitStruct, FLASH_LATENCY_1) != HAL_OK)
  {
    Error_Handler();
  }
  PeriphClkInit.PeriphClockSelection = RCC_PERIPHCLK_USB|RCC_PERIPHCLK_USART1;
  PeriphClkInit.Usart1ClockSelection = RCC_USART1CLKSOURCE_PCLK1;
  PeriphClkInit.UsbClockSelection = RCC_USBCLKSOURCE_HSI48;

  if (HAL_RCCEx_PeriphCLKConfig(&PeriphClkInit) != HAL_OK)
  {
    Error_Handler();
  }
}

/**
  * @brief ADC Initialization Function
  * @param None
  * @retval None
  */
static void MX_ADC_Init(void)
{

  /* USER CODE BEGIN ADC_Init 0 */

  /* USER CODE END ADC_Init 0 */

  ADC_ChannelConfTypeDef sConfig = {0};

  /* USER CODE BEGIN ADC_Init 1 */

  /* USER CODE END ADC_Init 1 */

  /** Configure the global features of the ADC (Clock, Resolution, Data Alignment and number of conversion)
  */
  hadc.Instance = ADC1;
  hadc.Init.ClockPrescaler = ADC_CLOCK_ASYNC_DIV1;
  hadc.Init.Resolution = ADC_RESOLUTION_12B;
  hadc.Init.DataAlign = ADC_DATAALIGN_RIGHT;
  hadc.Init.ScanConvMode = ADC_SCAN_DIRECTION_FORWARD;
  hadc.Init.EOCSelection = ADC_EOC_SEQ_CONV;
  hadc.Init.LowPowerAutoWait = DISABLE;
  hadc.Init.LowPowerAutoPowerOff = DISABLE;
  hadc.Init.ContinuousConvMode = DISABLE;
  hadc.Init.DiscontinuousConvMode = DISABLE;
  hadc.Init.ExternalTrigConv = ADC_SOFTWARE_START;
  hadc.Init.ExternalTrigConvEdge = ADC_EXTERNALTRIGCONVEDGE_NONE;
  hadc.Init.DMAContinuousRequests = DISABLE;
  hadc.Init.Overrun = ADC_OVR_DATA_PRESERVED;
  if (HAL_ADC_Init(&hadc) != HAL_OK)
  {
    Error_Handler();
  }

  /** Configure for the selected ADC regular channel to be converted.
  */
  sConfig.Channel = ADC_CHANNEL_8;
  sConfig.Rank = ADC_RANK_CHANNEL_NUMBER;
  sConfig.SamplingTime = ADC_SAMPLETIME_1CYCLE_5;
  if (HAL_ADC_ConfigChannel(&hadc, &sConfig) != HAL_OK)
  {
    Error_Handler();
  }
  /* USER CODE BEGIN ADC_Init 2 */

  /* USER CODE END ADC_Init 2 */

}

/**
  * @brief SPI1 Initialization Function
  * @param None
  * @retval None
  */
static void MX_SPI1_Init(void)
{

  /* USER CODE BEGIN SPI1_Init 0 */

  /* USER CODE END SPI1_Init 0 */

  /* USER CODE BEGIN SPI1_Init 1 */

  /* USER CODE END SPI1_Init 1 */
  /* SPI1 parameter configuration*/
  hspi1.Instance = SPI1;
  hspi1.Init.Mode = SPI_MODE_MASTER;
  hspi1.Init.Direction = SPI_DIRECTION_2LINES;
  hspi1.Init.DataSize = SPI_DATASIZE_8BIT;
  hspi1.Init.CLKPolarity = SPI_POLARITY_LOW;
  hspi1.Init.CLKPhase = SPI_PHASE_1EDGE;
  hspi1.Init.NSS = SPI_NSS_SOFT;
  hspi1.Init.BaudRatePrescaler = SPI_BAUDRATEPRESCALER_2;
  hspi1.Init.FirstBit = SPI_FIRSTBIT_MSB;
  hspi1.Init.TIMode = SPI_TIMODE_DISABLE;
  hspi1.Init.CRCCalculation = SPI_CRCCALCULATION_DISABLE;
  hspi1.Init.CRCPolynomial = 7;
  hspi1.Init.CRCLength = SPI_CRC_LENGTH_DATASIZE;
  hspi1.Init.NSSPMode = SPI_NSS_PULSE_ENABLE;
  if (HAL_SPI_Init(&hspi1) != HAL_OK)
  {
    Error_Handler();
  }
  /* USER CODE BEGIN SPI1_Init 2 */

  /* USER CODE END SPI1_Init 2 */

}

/**
  * @brief SPI2 Initialization Function
  * @param None
  * @retval None
  */
static void MX_SPI2_Init(void)
{

  /* USER CODE BEGIN SPI2_Init 0 */

  /* USER CODE END SPI2_Init 0 */

  /* USER CODE BEGIN SPI2_Init 1 */

  /* USER CODE END SPI2_Init 1 */
  /* SPI2 parameter configuration*/
  hspi2.Instance = SPI2;
  hspi2.Init.Mode = SPI_MODE_MASTER;
  hspi2.Init.Direction = SPI_DIRECTION_2LINES;
  hspi2.Init.DataSize = SPI_DATASIZE_8BIT;
  hspi2.Init.CLKPolarity = SPI_POLARITY_LOW;
  hspi2.Init.CLKPhase = SPI_PHASE_1EDGE;
  hspi2.Init.NSS = SPI_NSS_SOFT;
  hspi2.Init.BaudRatePrescaler = SPI_BAUDRATEPRESCALER_2;
  hspi2.Init.FirstBit = SPI_FIRSTBIT_MSB;
  hspi2.Init.TIMode = SPI_TIMODE_DISABLE;
  hspi2.Init.CRCCalculation = SPI_CRCCALCULATION_DISABLE;
  hspi2.Init.CRCPolynomial = 7;
  hspi2.Init.CRCLength = SPI_CRC_LENGTH_DATASIZE;
  hspi2.Init.NSSPMode = SPI_NSS_PULSE_ENABLE;
  if (HAL_SPI_Init(&hspi2) != HAL_OK)
  {
    Error_Handler();
  }
  /* USER CODE BEGIN SPI2_Init 2 */

  /* USER CODE END SPI2_Init 2 */

}

/**
  * @brief TIM3 Initialization Function
  * @param None
  * @retval None
  */
static void MX_TIM3_Init(void)
{

  /* USER CODE BEGIN TIM3_Init 0 */

  /* USER CODE END TIM3_Init 0 */

  TIM_ClockConfigTypeDef sClockSourceConfig = {0};
  TIM_MasterConfigTypeDef sMasterConfig = {0};

  /* USER CODE BEGIN TIM3_Init 1 */

  /* USER CODE END TIM3_Init 1 */
  htim3.Instance = TIM3;
  htim3.Init.Prescaler = 500-1;
  htim3.Init.CounterMode = TIM_COUNTERMODE_UP;
  htim3.Init.Period = 360-1;
  htim3.Init.ClockDivision = TIM_CLOCKDIVISION_DIV1;
  htim3.Init.AutoReloadPreload = TIM_AUTORELOAD_PRELOAD_DISABLE;
  if (HAL_TIM_Base_Init(&htim3) != HAL_OK)
  {
    Error_Handler();
  }
  sClockSourceConfig.ClockSource = TIM_CLOCKSOURCE_INTERNAL;
  if (HAL_TIM_ConfigClockSource(&htim3, &sClockSourceConfig) != HAL_OK)
  {
    Error_Handler();
  }
  sMasterConfig.MasterOutputTrigger = TIM_TRGO_RESET;
  sMasterConfig.MasterSlaveMode = TIM_MASTERSLAVEMODE_DISABLE;
  if (HAL_TIMEx_MasterConfigSynchronization(&htim3, &sMasterConfig) != HAL_OK)
  {
    Error_Handler();
  }
  /* USER CODE BEGIN TIM3_Init 2 */

  /* USER CODE END TIM3_Init 2 */

}
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

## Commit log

2025-04-28 mcad ecad BOM readme
    [DAUGHTER.SchDoc, NEAR.SchDoc, NEAR_DAUGHTER.PcbDoc, NEAR_DAUGHTER.SchDoc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]
2025-05-20 resin cover for the screen which always breakcs
    [anchor-screen-cover.dwg, anchor-screen-cover.ipt, anchor-screen-cover.stl]
